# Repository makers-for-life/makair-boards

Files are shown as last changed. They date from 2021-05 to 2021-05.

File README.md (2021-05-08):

# MakAir Boards

## Components

| Part | Version | Last Changelog | Ready? | Schematics |
| ---- | ------- | -------------- | ------ | ---------- |
| [Pinch Valve Controller](./src/pinch-valve-controller) | V1 | Initial design | ✅ | [view schematic](./src/pinch-valve-controller/schematics/V1/1782SC001_01.pdf)
| [Raspberry Pi RTC](./src/raspberry-pi-rtc) | V1 | Initial design | ✅ | none
| [SFM 3300 Adapter](./src/sfm-3300-adapter) | V1 | Initial design | ✅ | none

## Renders

### The "Pinch Valve Controller"

<p align="center">
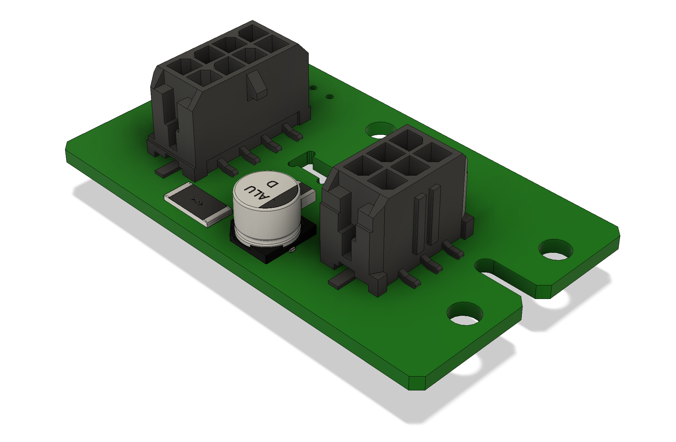
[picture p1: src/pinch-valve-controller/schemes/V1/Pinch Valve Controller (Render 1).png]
Pinch Valve Controller Render
  
</p>

### The "Raspberry Pi RTC"

<p align="center">
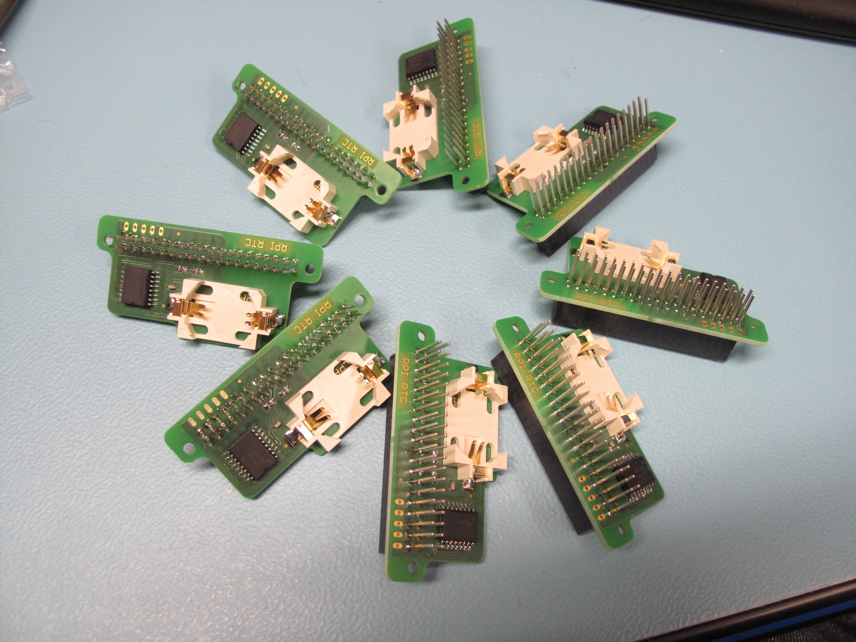
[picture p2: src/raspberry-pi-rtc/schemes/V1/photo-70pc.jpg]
Raspberry Pi RTC Photo
  
</p>

### The "SFM 3300 Adapter"

<p align="center">
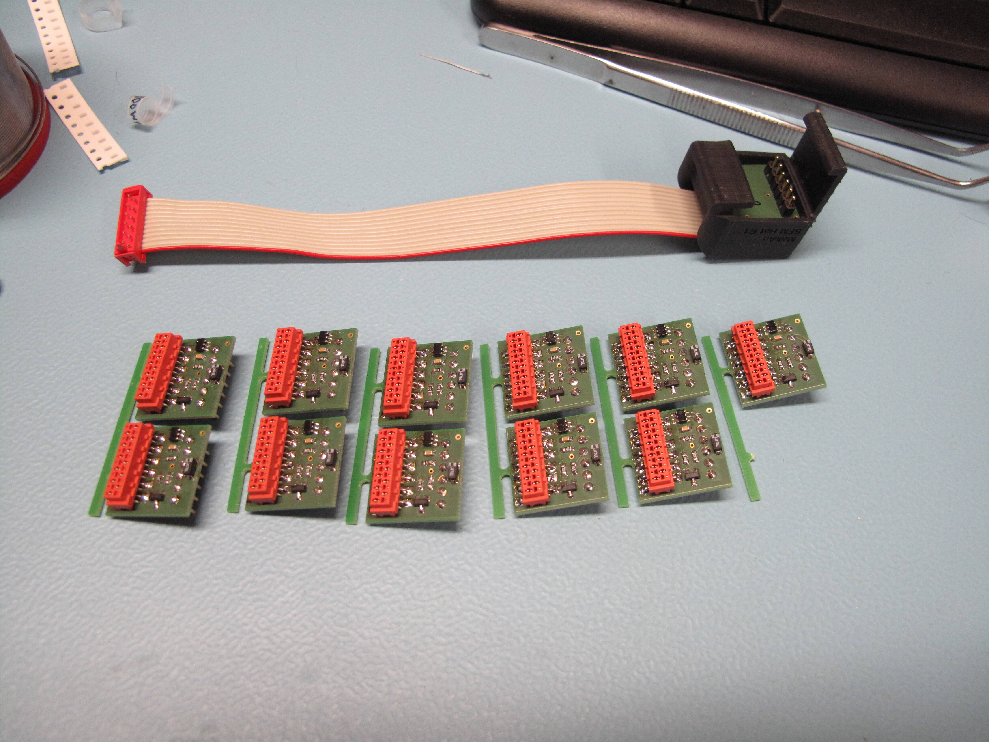
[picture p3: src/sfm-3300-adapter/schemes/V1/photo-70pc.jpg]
SFM 3300 Adapter Photo
  
</p>

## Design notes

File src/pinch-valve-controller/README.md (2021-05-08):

# Pinch Valve Controller

## Versions

| Version | Last Changelog | Ready? |
| ------- | -------------- | ------ |
| V1 | Initial design | ✅

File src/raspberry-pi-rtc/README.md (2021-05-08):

# Raspberry Pi RTC

## Versions

| Version | Last Changelog | Ready? |
| ------- | -------------- | ------ |
| V1 | Initial design | ✅

## Notes

This RTC HAT was designed to avoid any conflict between Raspberry Pi touchscreen and RTC. All the RTC you can find are connected on SDA3/SCL3 of the Raspberry 4. But the touchscreen is already connected to this port, and there is some random issues.

So, this small board is designed to connect a DS3231 on I2C6 of the Raspberry 4 (pin 15 and 16).

### How to setup RTC on I2C6 of Raspberry 4

Make sure that the Raspberry Pi is up to date:

```
sudo apt update
sudo apt upgrade
sudo reboot
sudo rpi-update
```

* Append to `/boot/config.txt`:

`dtoverlay=i2c6`

* Make a new DTC from the existing RTC one (named `i2c6-rtc`);

`sudo dtc -I dtb -O dts /boot/overlays/i2c-rtc.dtbo -o /boot/overlays/i2c6-rtc.dts`

* Edit it to change `i2c_arm` to `i2c6`:

`sudo sed -i "s/i2c_arm/i2c6/g" /boot/overlays/i2c6-rtc.dts`

* Recompile it:

`sudo dtc -I dts -O dtb /boot/overlays/i2c6-rtc.dts -o /boot/overlays/i2c6-rtc.dtbo`

* Append to `/boot/config.txt`:

`dtoverlay=i2c6-rtc,ds3231`

After reboot, check `dmesg`:

```
dmesg | grep rtc
[    5.883603] rtc : registered as rtc0
```

If battery is low:

```
[  42.117539] rtc: low voltage detected, time is unreliable
```

Now write current time into the RTC, make sure your Raspberry Pi clock is synchronized, using `date`, then `sudo hwclock -w` to write current date into the RTC.

On Arch Linux, you have to create a script on startup to read RTC time during the boot:

```
cat > /etc/systemd/system/rtc.service << ENDRTCSERVICE
[Unit]
Description=RTClock
Before=network.target

[Service]
ExecStart=/usr/bin/hwclock -s
Type=oneshot
[Install]
WantedBy=multi-user.target
ENDRTCSERVICE
```

Then enable this service:

```
systemctl enable rtc
systemctl start rtc
```

Reboot, then check everything is OK:

```
journalctl -u rtc
```

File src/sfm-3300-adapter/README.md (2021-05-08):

# SFM 3300 Adapter

## Versions

| Version | Last Changelog | Ready? |
| ------- | -------------- | ------ |
| V1 | Initial design | ✅

## Notes

This little board provides a convenient way to interface a Sensirion SFM3300 to the red micromatch connector of the Motherboard.

As soon I2C clock remains low, the sensor is shutdown. This allows easy hard reset.

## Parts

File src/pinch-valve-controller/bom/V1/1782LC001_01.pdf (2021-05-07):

Designation : INTERFACE MOTEUR | | Author by : olbonneau
Customer : TRONICO | Date : 23/04/2020 | Signature :
Reference : 1782LC001 | Revision : 01A | Verified by : P. Boiziau
Customer Reference : 099 | | Signature :
Designator | ID_RnD | CODE_PC | Quantity | Done
* | | C1 | 21U00041 | 002504131A | COND_ALUM CMS D:6.3mm | 47uF 50V 20% 680mR -55°C/+105°C | PANASONIC EEEFT1H470AP | 1
* | | C2,C3 | 23U00347 | 00280K614A | COND_CERAM CMS 0603 X5R | 1uF 50V 10% -55°C/+85°C | TAIYO YUDEN UMK107BJ105KA-T TDK CGA3E3X5R1H105K080AB | 2
* | | C4 | 23U00036 | 002806597A | COND_CERAM CMS 0603 X7R | 100nF 50V 10% -55°C/+125°C | KEMET C0603C104K5RAC VISHAY VJ0603Y104KXAAT AVX 06035C104KAT2A | 1
* | | C6 | 23U00488 | 00280K521A | COND_CERAM CMS 1206 X5R | 10uF 50V 10% -55°C/+85°C | MURATA GRM31CR61H106KA12L | 1
* | | ET1 | G1U00004 | - | ETIQUETTE IDENTIFICATION | 1782ET001 | PLAN 1782ET001 IND01 | 1
| * | - | - | CONSOM1071 | ETIQU ETIQU POLYIMIDE AMBRE MAT | | BRADY THT-46-724-10 | 1
* | | J1 | A7U00233 | 005168584A-RD | CONNECT MICRO-FIT CMS 2x4PTS | EMBASE RECT MALE DROIT -40°C/+105°C | MOLEX 43045-0818 | 1
* | | J2 | A7U00234 | 005168586A-RD | CONNECT MICRO-FIT CMS 2x3PTS | EMBASE RECT MALE DROIT -40°C/+105°C | MOLEX 43045-0618 | 1
* | | L1 | 42U00104 | 003114209A-RD | SELF CMS 2.5x2mm | 1.5uH 20% 3.1A -55°C/+125°C | VISHAY IHHP1008ABER1R5M01 | 1
* | | PCB1 | I1U00004 | 00590G849A | CIRCUIT IMPRIME INTERFACE MOTEUR | 1782CI001 | SPECIF 1782PCB001 IND01 PLANS 1782CI001 IND01 GERBERS 1782GER001 IND01 | 1 | Mise en panneau faite par le fournisseur
* | | R1 | 11U00106 | 00140AA309A-RD | REST CMS 0603 100PPM | 220R 1/10W 1% -55°C/+155°C | YAGEO RC0603FR-07220RL | 1
* | | R2,R7 | 11U00108 | 00140D722A | REST CMS 0603 100PPM | 10kR 1/10W 1% -55°C/+155°C | NEOHM CRG0603F10K YAGEO RC0603FR-0710KL VISHAY CRCW060310K0FKEA VISHAY CRCW060310K0FK@e3 | 2
* | | R3 | 11U00053 | 00140AA3641A | REST CMS 0603 100PPM | 330kR 1/10W 1% -55°C/+155°C | VISHAY CRCW0603330KFKEA | 1
* | | R4 | 11U00279 | 00140Q148A-RD | REST CMS 0805 100PPM | 270R 1/8W 1% -55°C/+155°C | YAGEO RC0805FR-07270RL | 1
* | | R5 | | | | | | NC
* | | R6 | 11U00688 | 00140AA3979A | REST CMS 0603 100PPM | 5.49kR 1/10W 1% -55°C/+155°C | YAGEO RC0603FR-075K49L | 1
* | | R8 | 11U01009 | 00140B064A | REST CMS 2512 100PPM | 1R 1.5W 1% 500V -55°C/+155°C | VISHAY CRCW25121R00FKEGHP | 1
* | | U1 | 61U00045 | 00480K448A-RD | CI_AOP_COMPAR CMS SOT23-5 | SINGLE COMP +2.7V/+5V R TO R -40°C/+85°C -65°C/+150°C | TEXAS INSTRUMENTS LMC7215IM5/NOPB | 1
* | | U2 | ECU00004 | 00480P154A | CAPTEUR_OPTO CMS 5.5x4x4 PHOTOTRANSISTOR | +1.0V/+1.4V NPN -40°C/+125°C -40°C/+125°C | VISHAY TCPT1350X01 | 1
Level | Reference designator | ID_RnD | Item Code | Description | Quantity | Commentary
1 | 2 | 3 | 4 | | | | Short Description | Long Description | Manufacturer & Part Number
Soudure : | SAC

26 RUE DU BOCAGE CS 20660
ST PHILBERT DE BOUAINE
85607 MONTAIGU CEDEX
Tél : +33 (0)2 51 41 91 35 Fax : +33 (0)2 51 41 94 27
ET68/D | STRICTEMENT CONFIDENTIEL TRONICO | 1/1

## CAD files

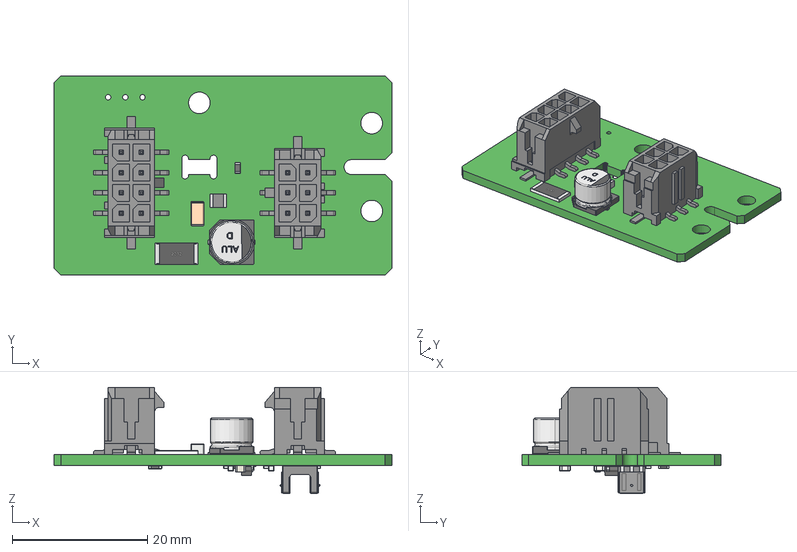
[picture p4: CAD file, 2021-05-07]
src/pinch-valve-controller/step/V1/1782CI001_01.step
50.0 x 29.5 x 15.7 mm
User_Library-SMD_RESISTOR-1
Extruded x 8
1206x160
0603x080 x 2
Corps x 7
Terminal x 14
Vishay_logo_-_1
Vishay_logo
SOT23-5-2
Fuss_1
Pins_1
K_X_F6rper_1
Beschriftung_1

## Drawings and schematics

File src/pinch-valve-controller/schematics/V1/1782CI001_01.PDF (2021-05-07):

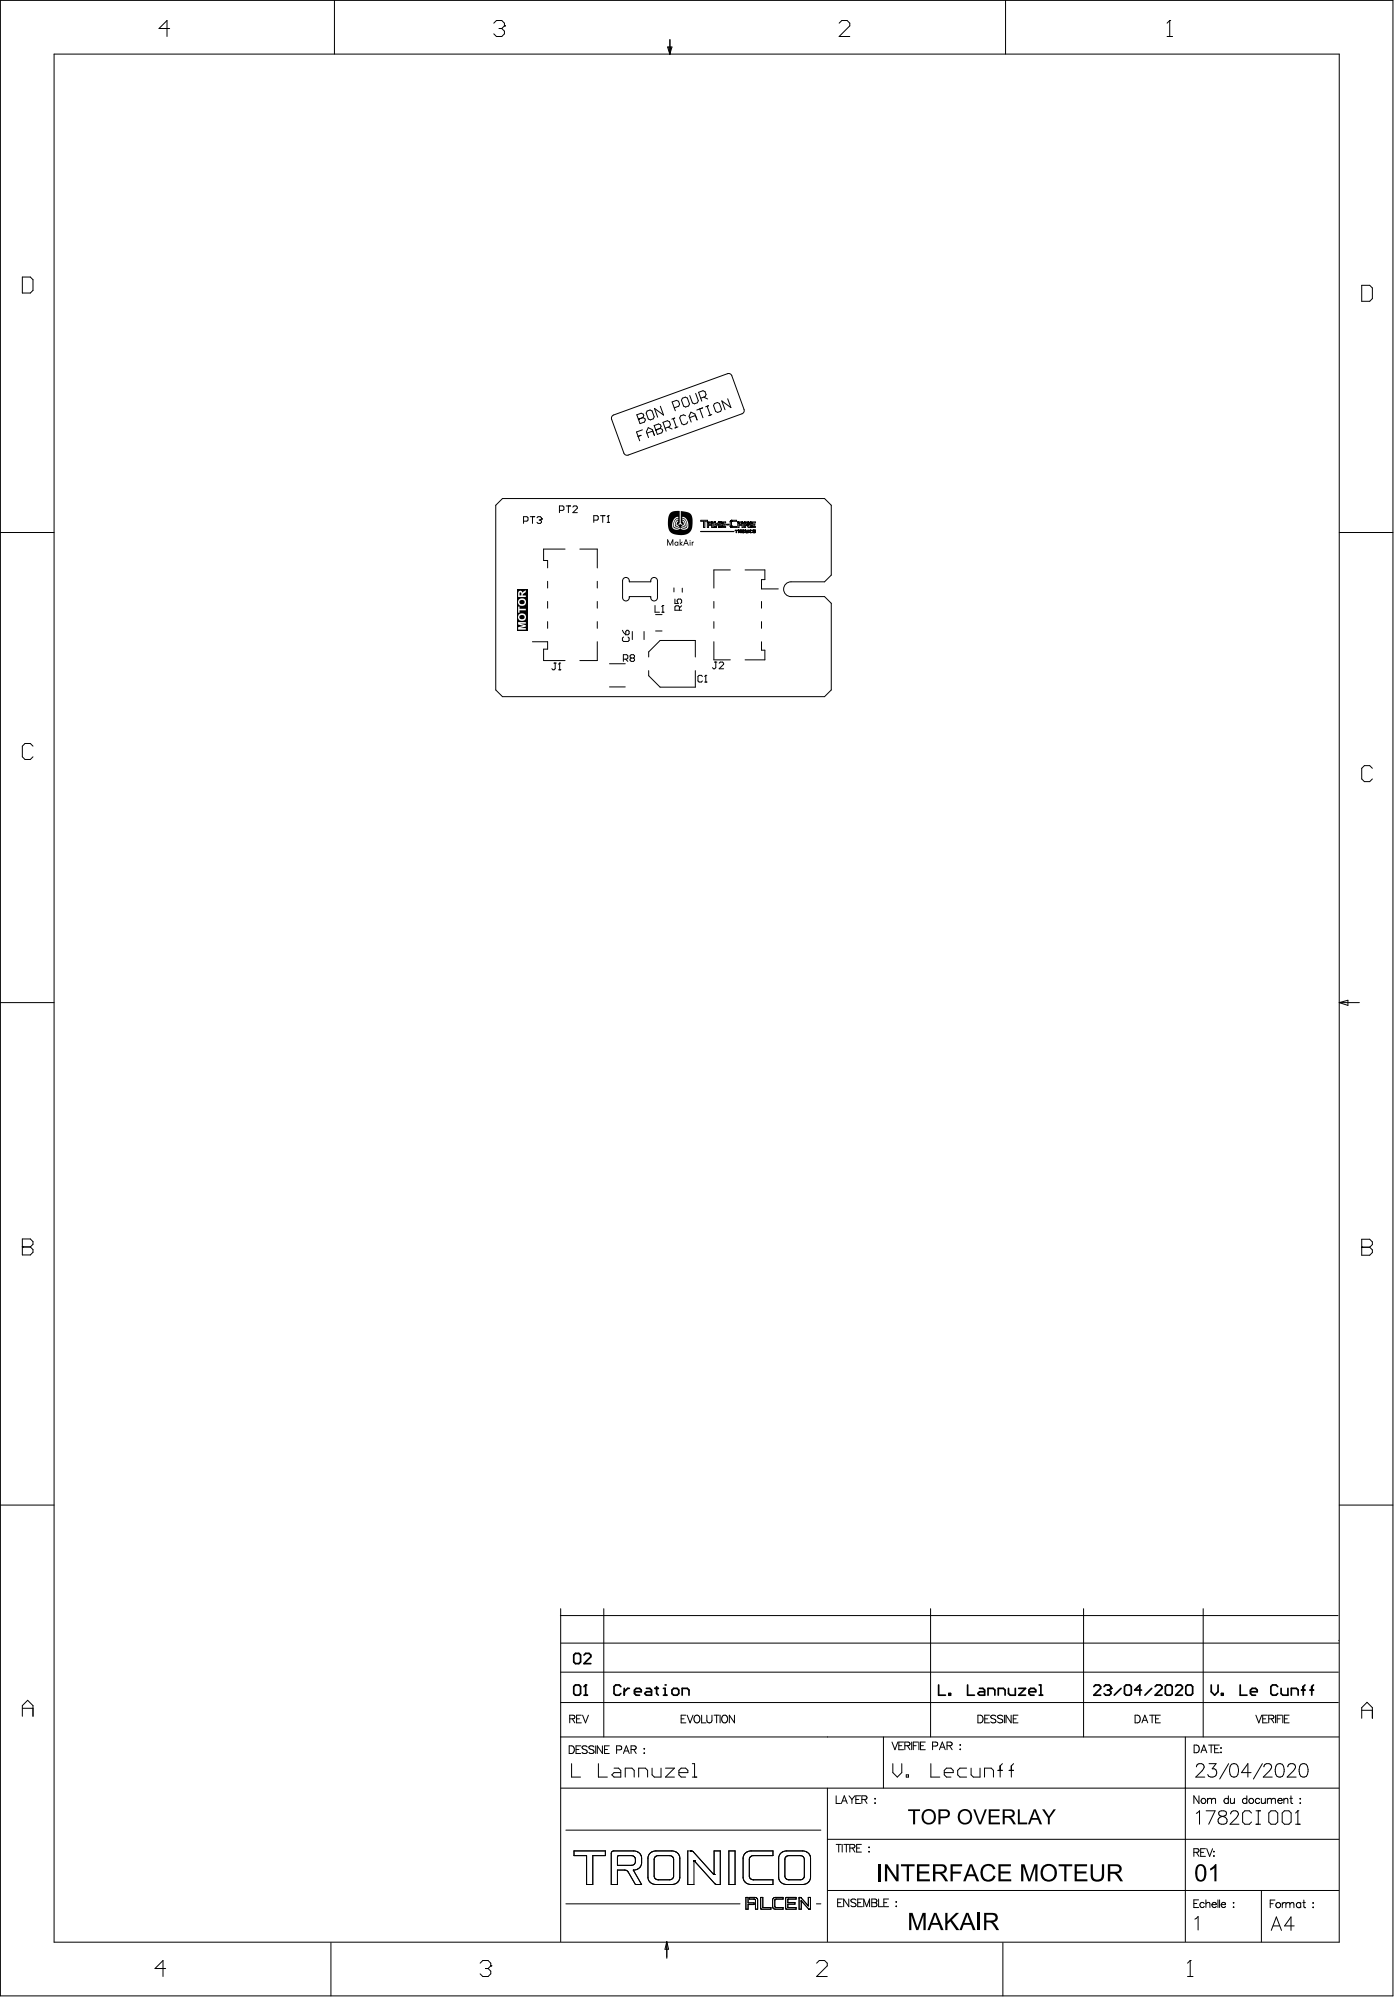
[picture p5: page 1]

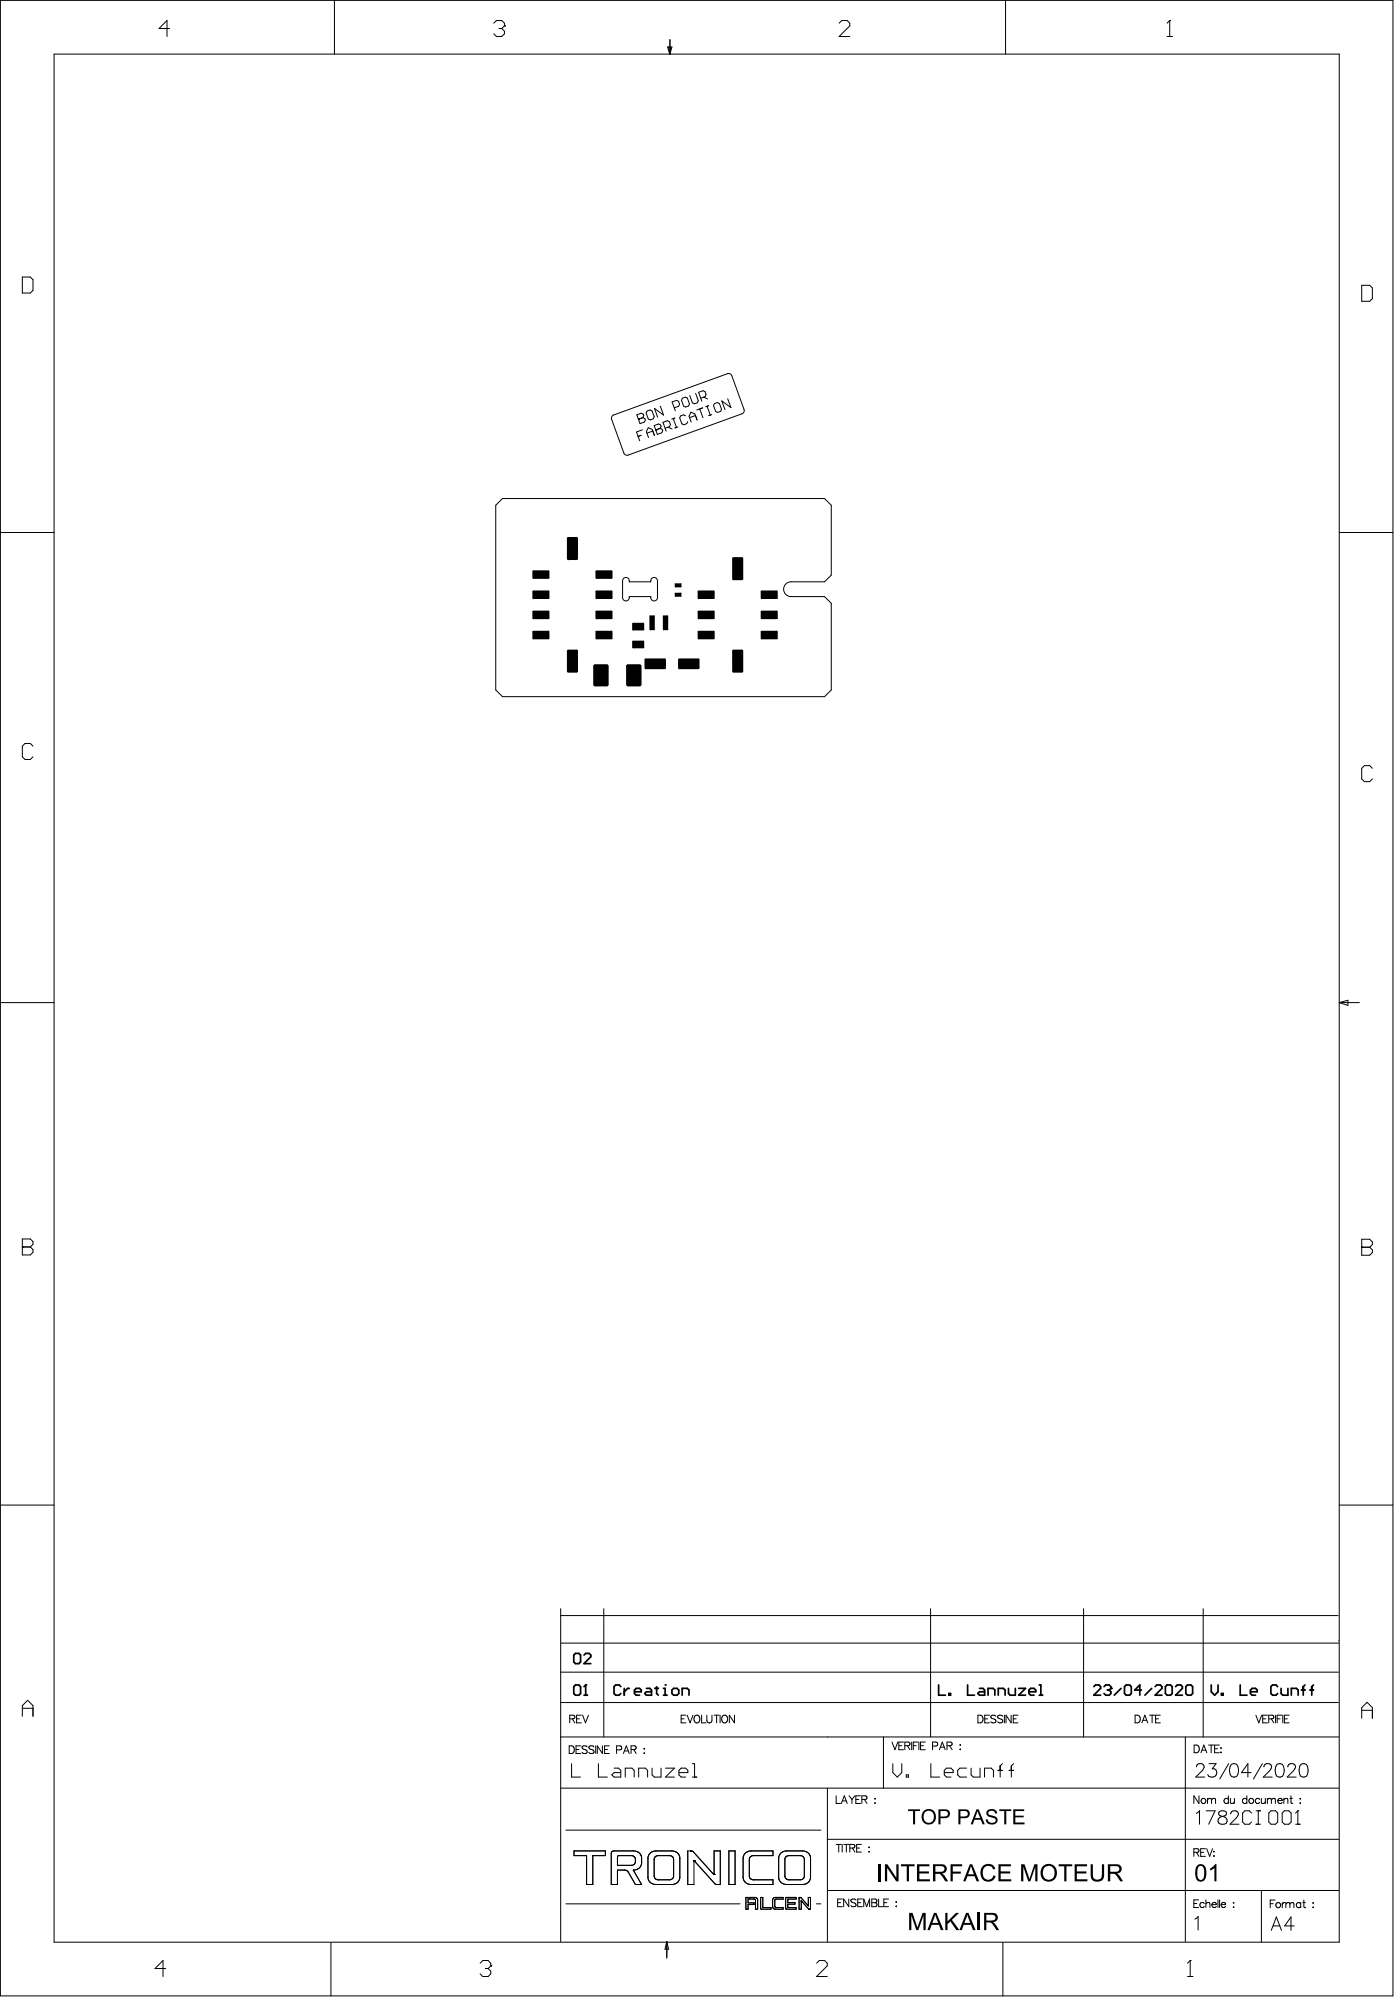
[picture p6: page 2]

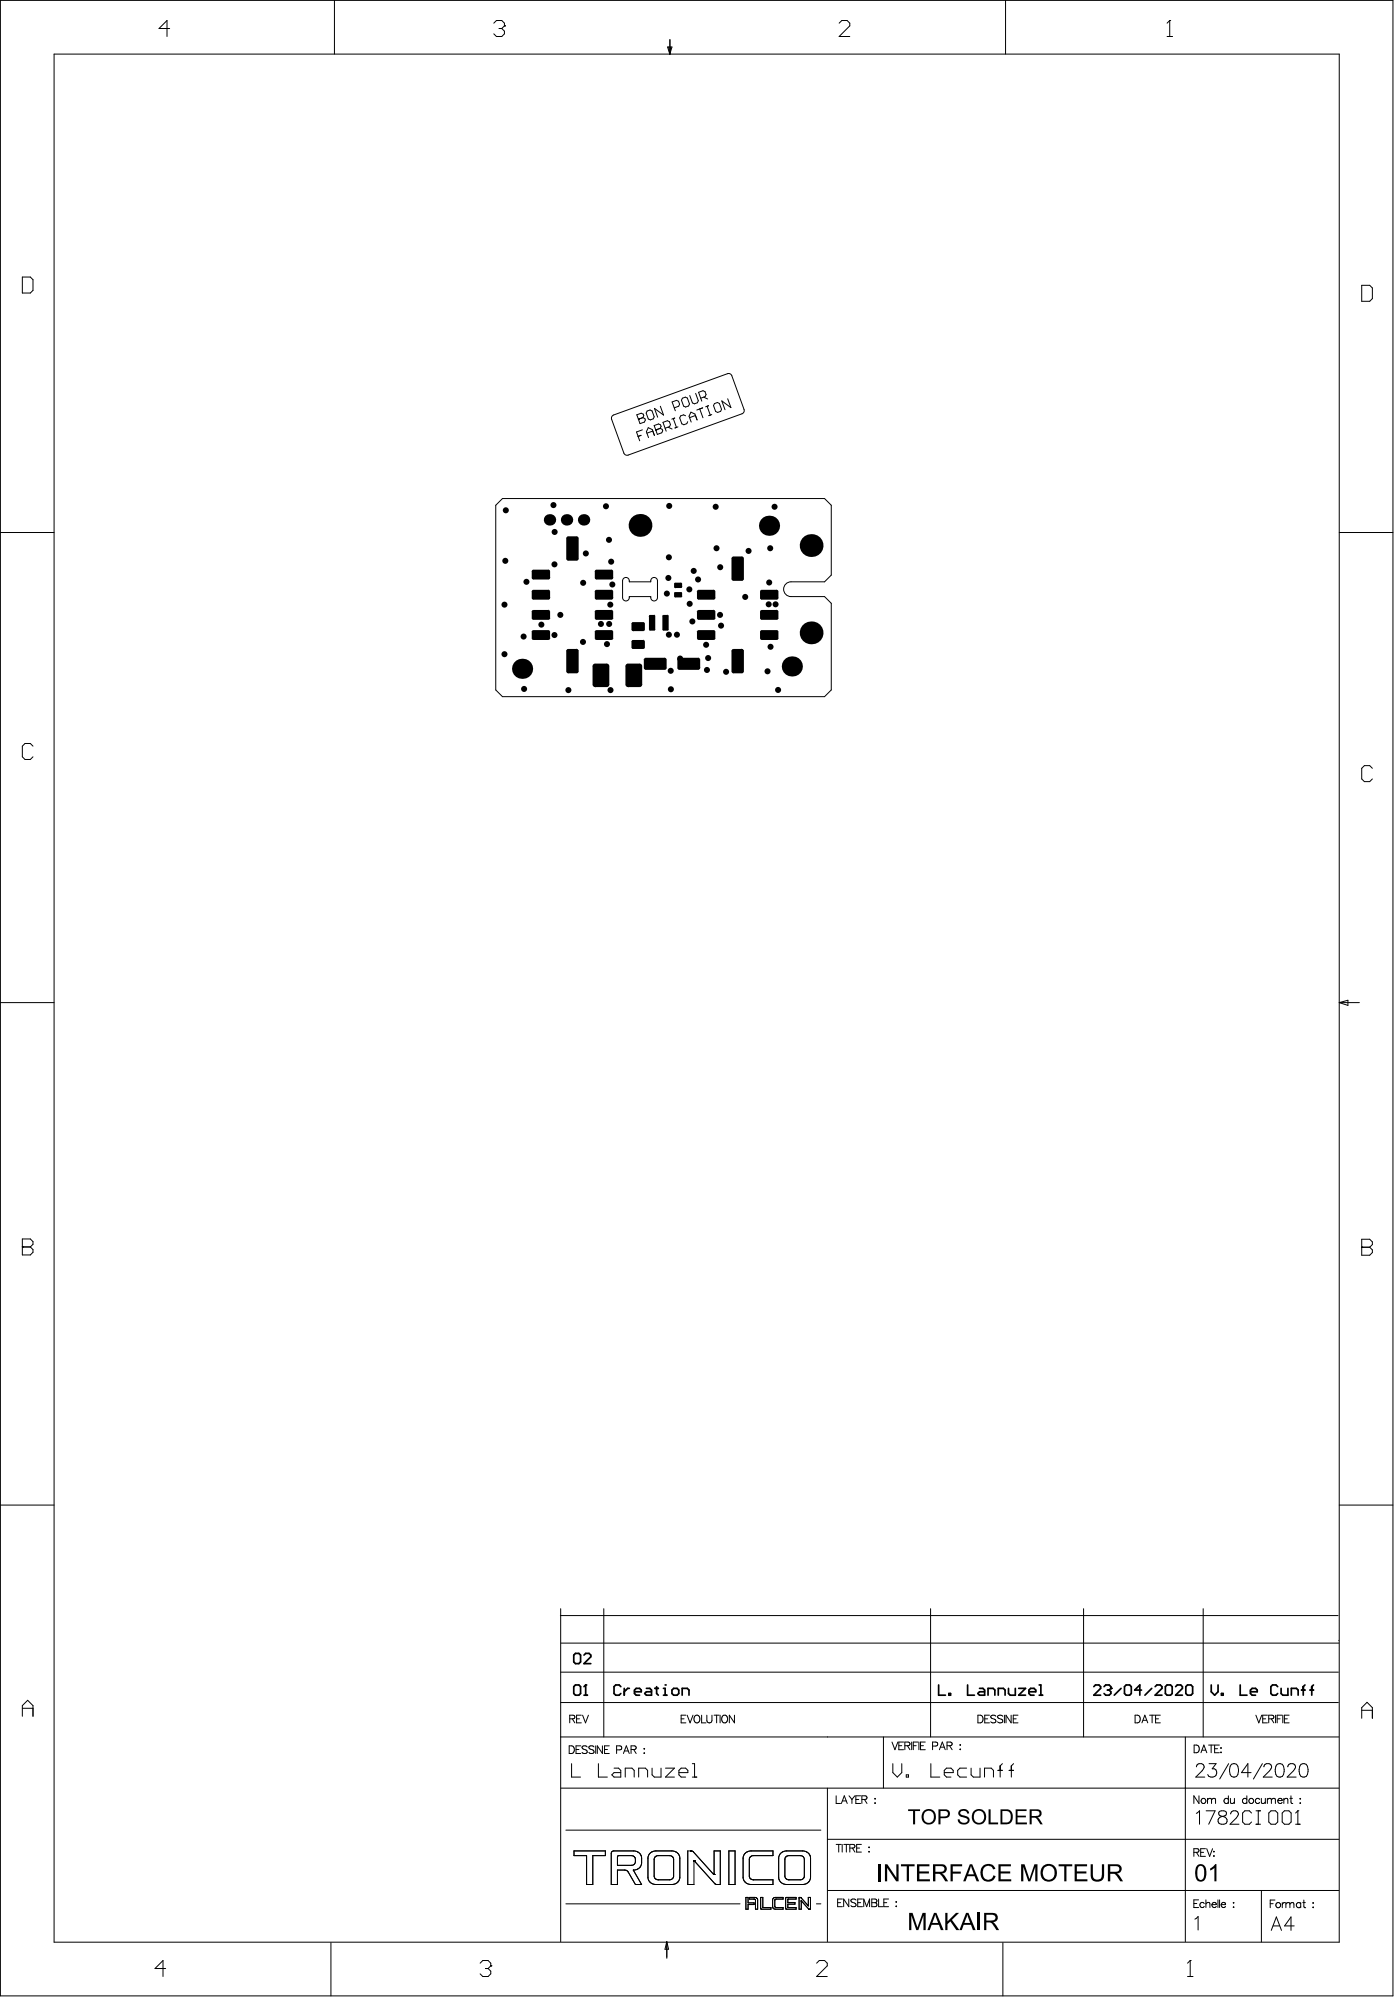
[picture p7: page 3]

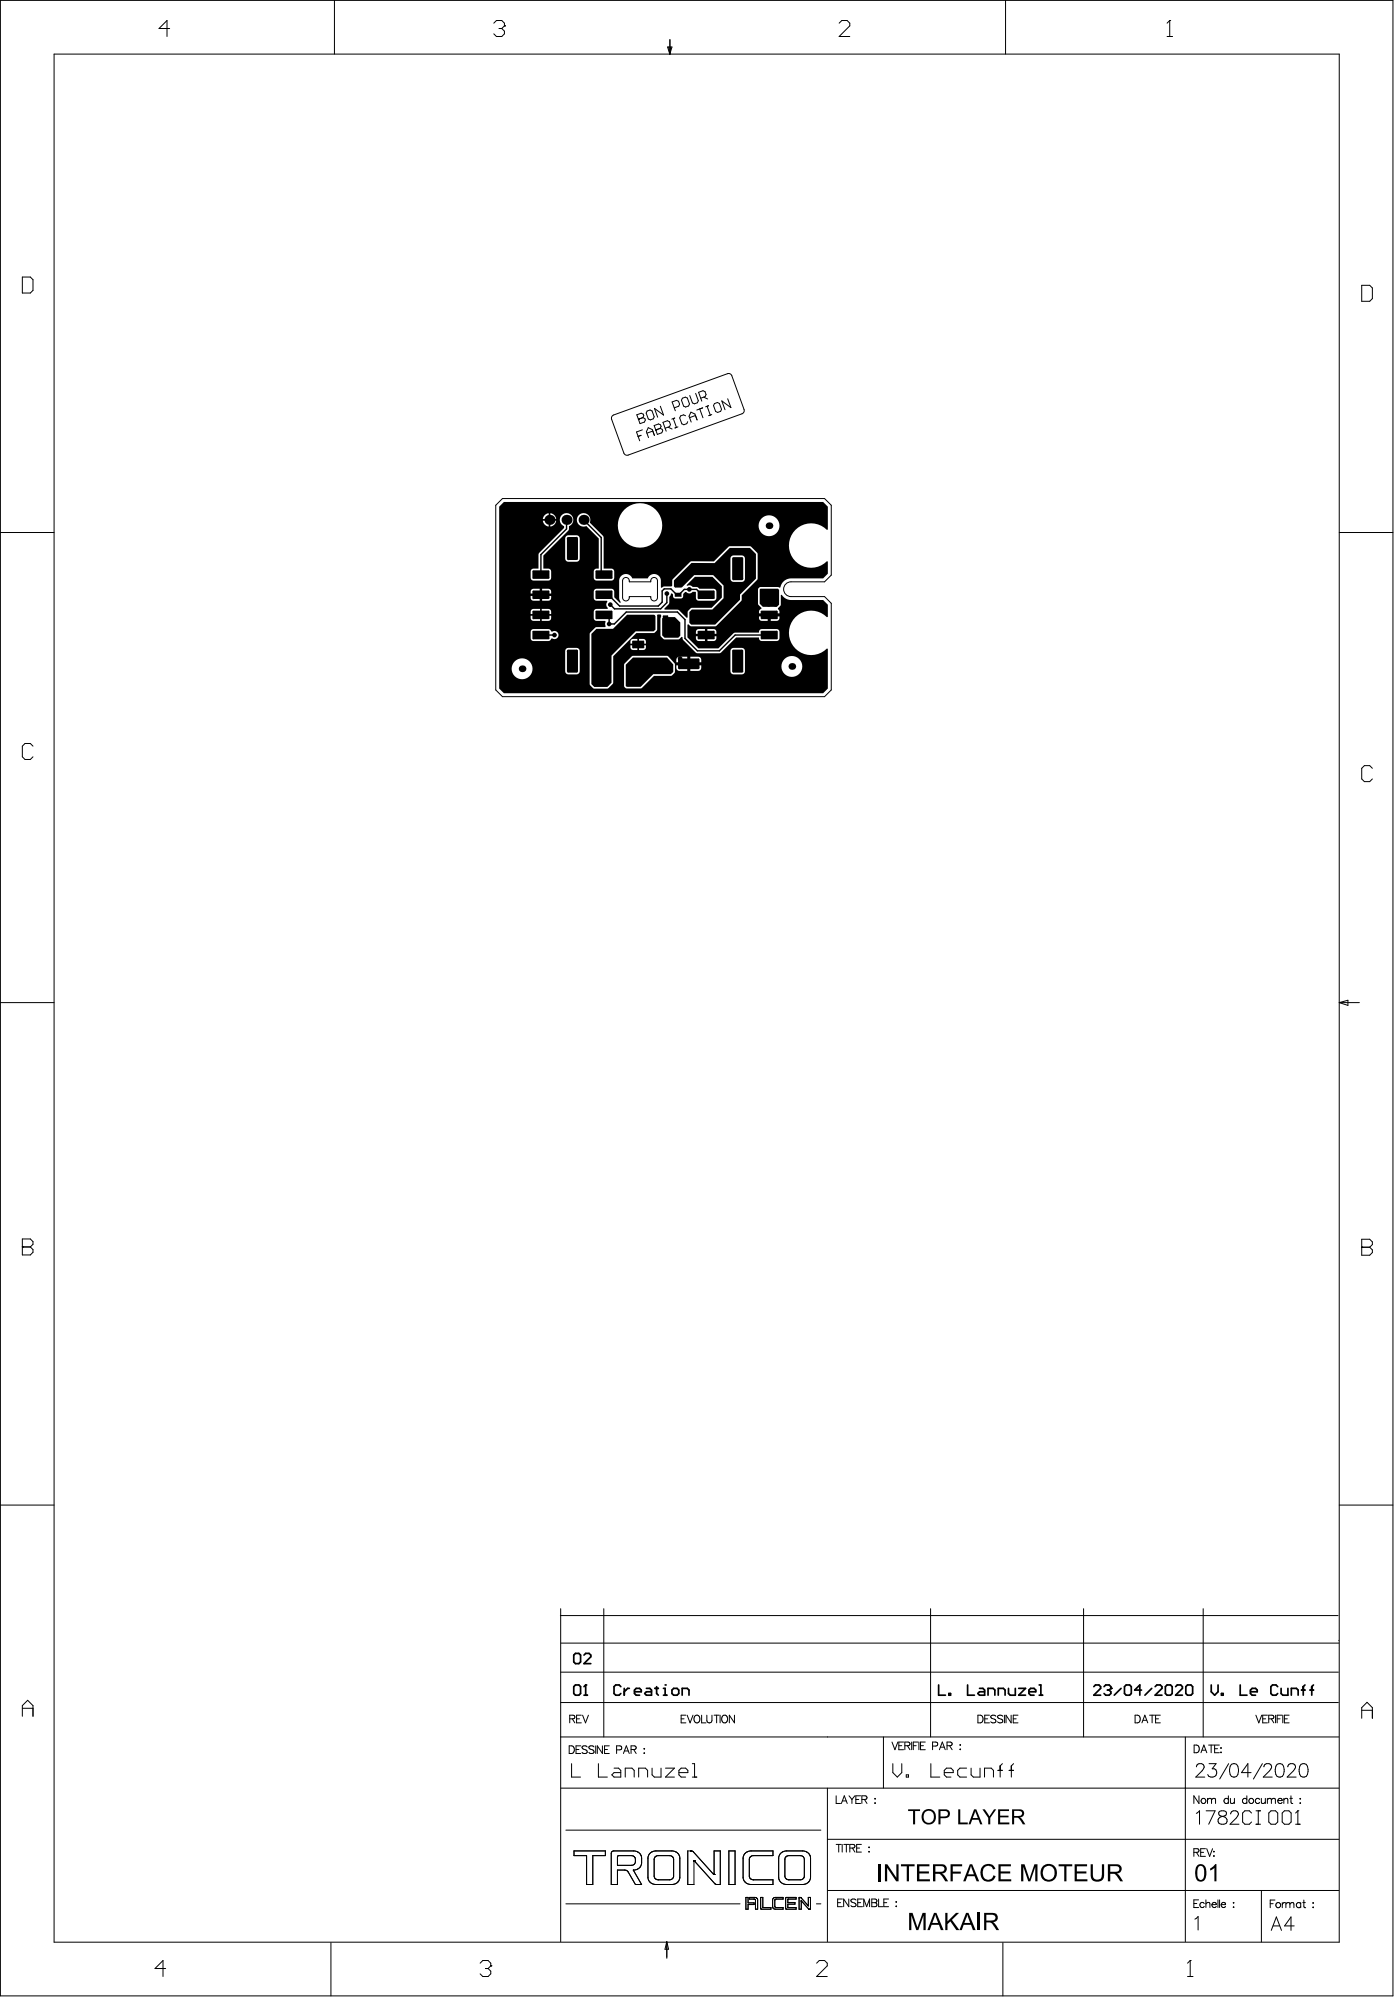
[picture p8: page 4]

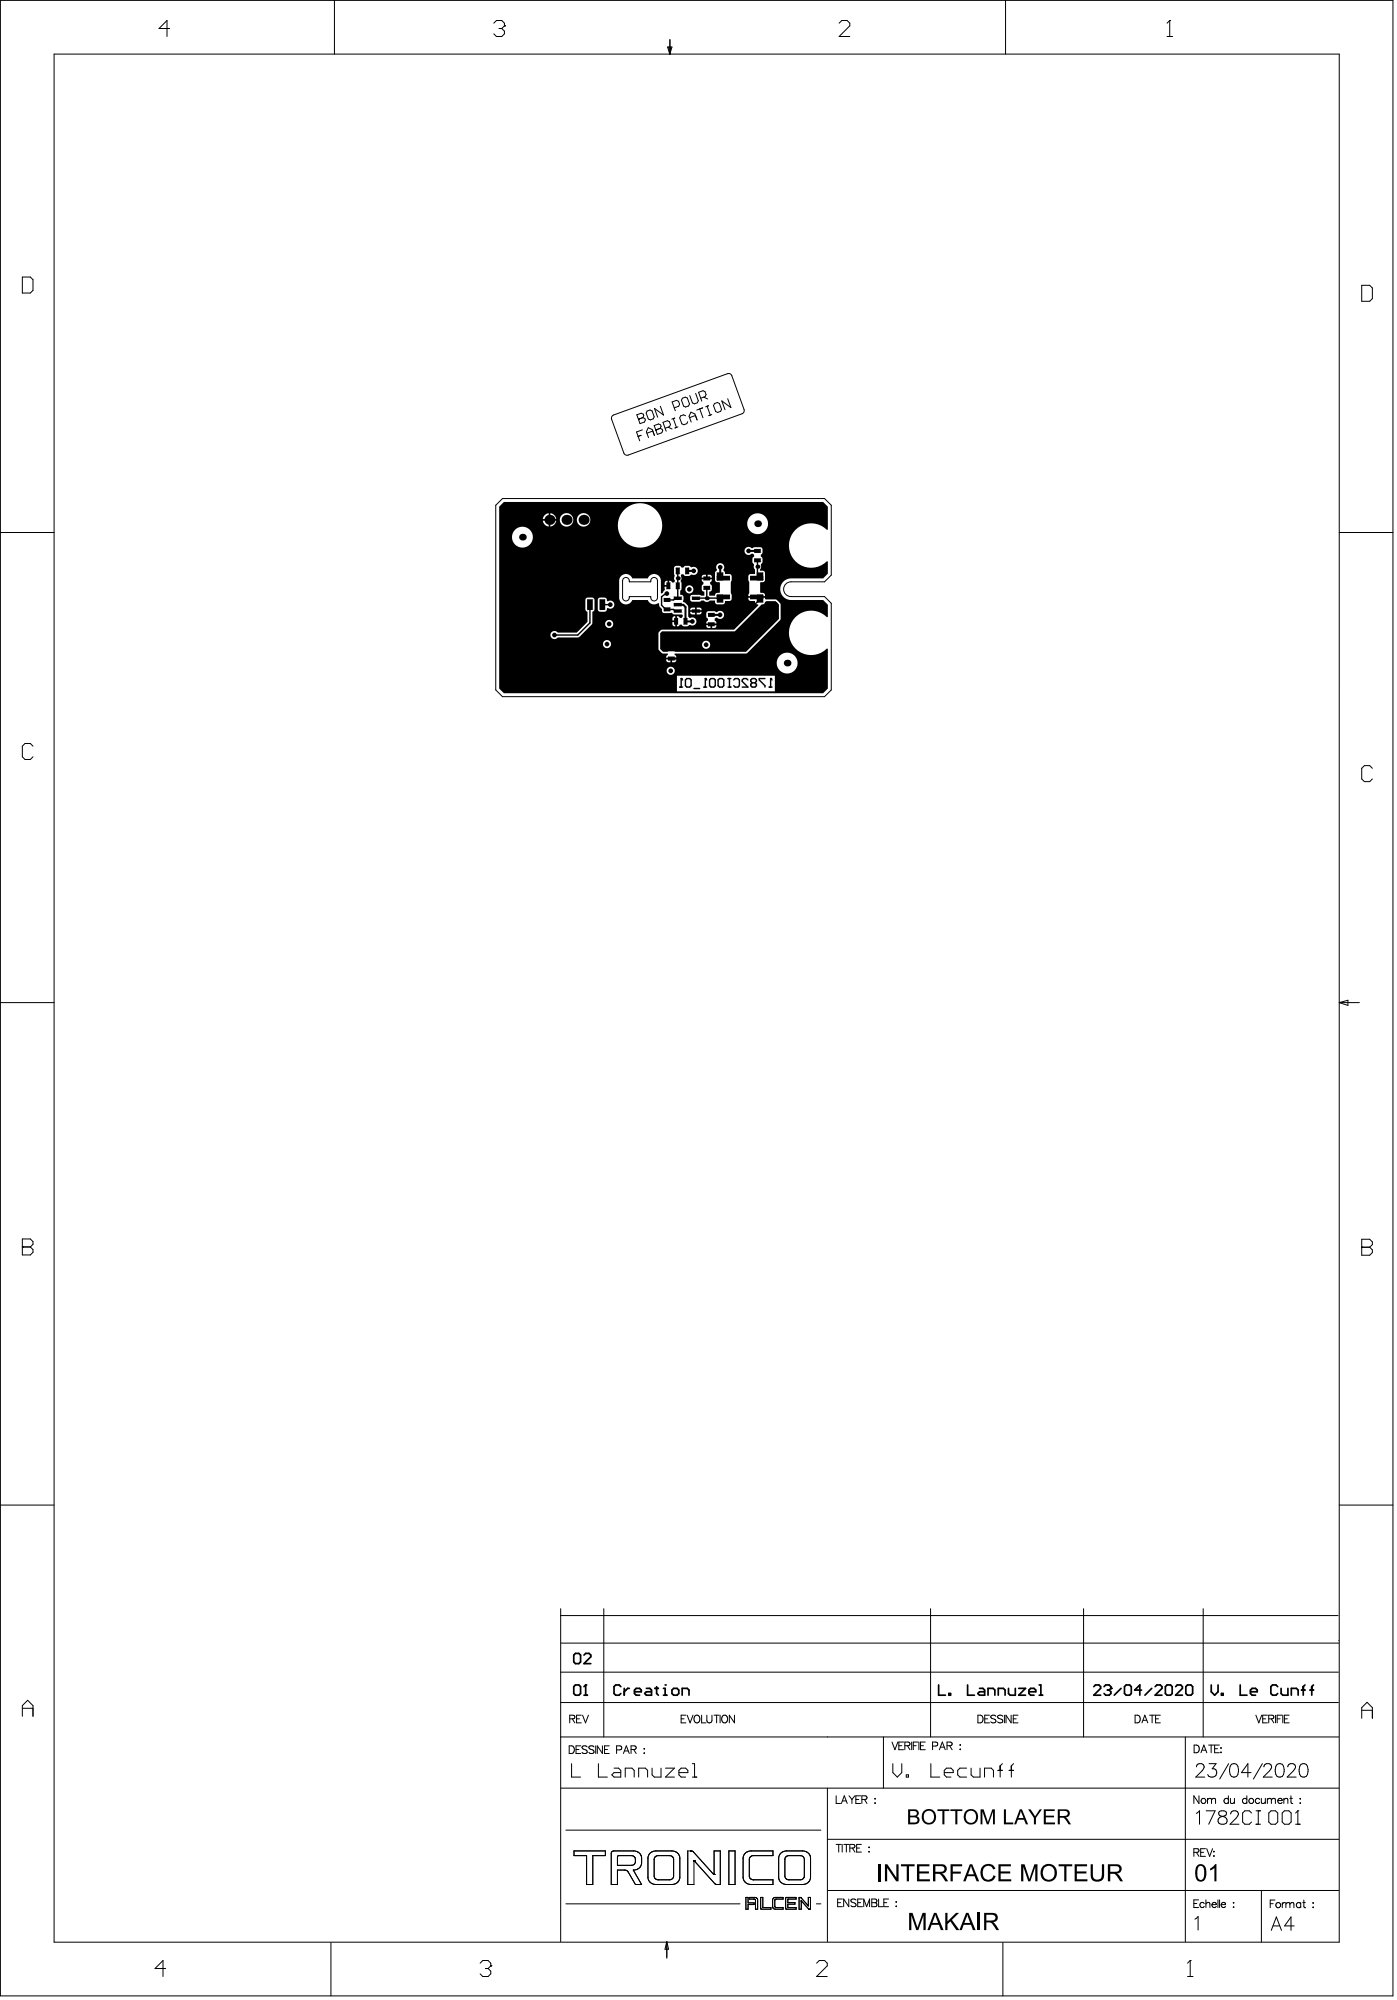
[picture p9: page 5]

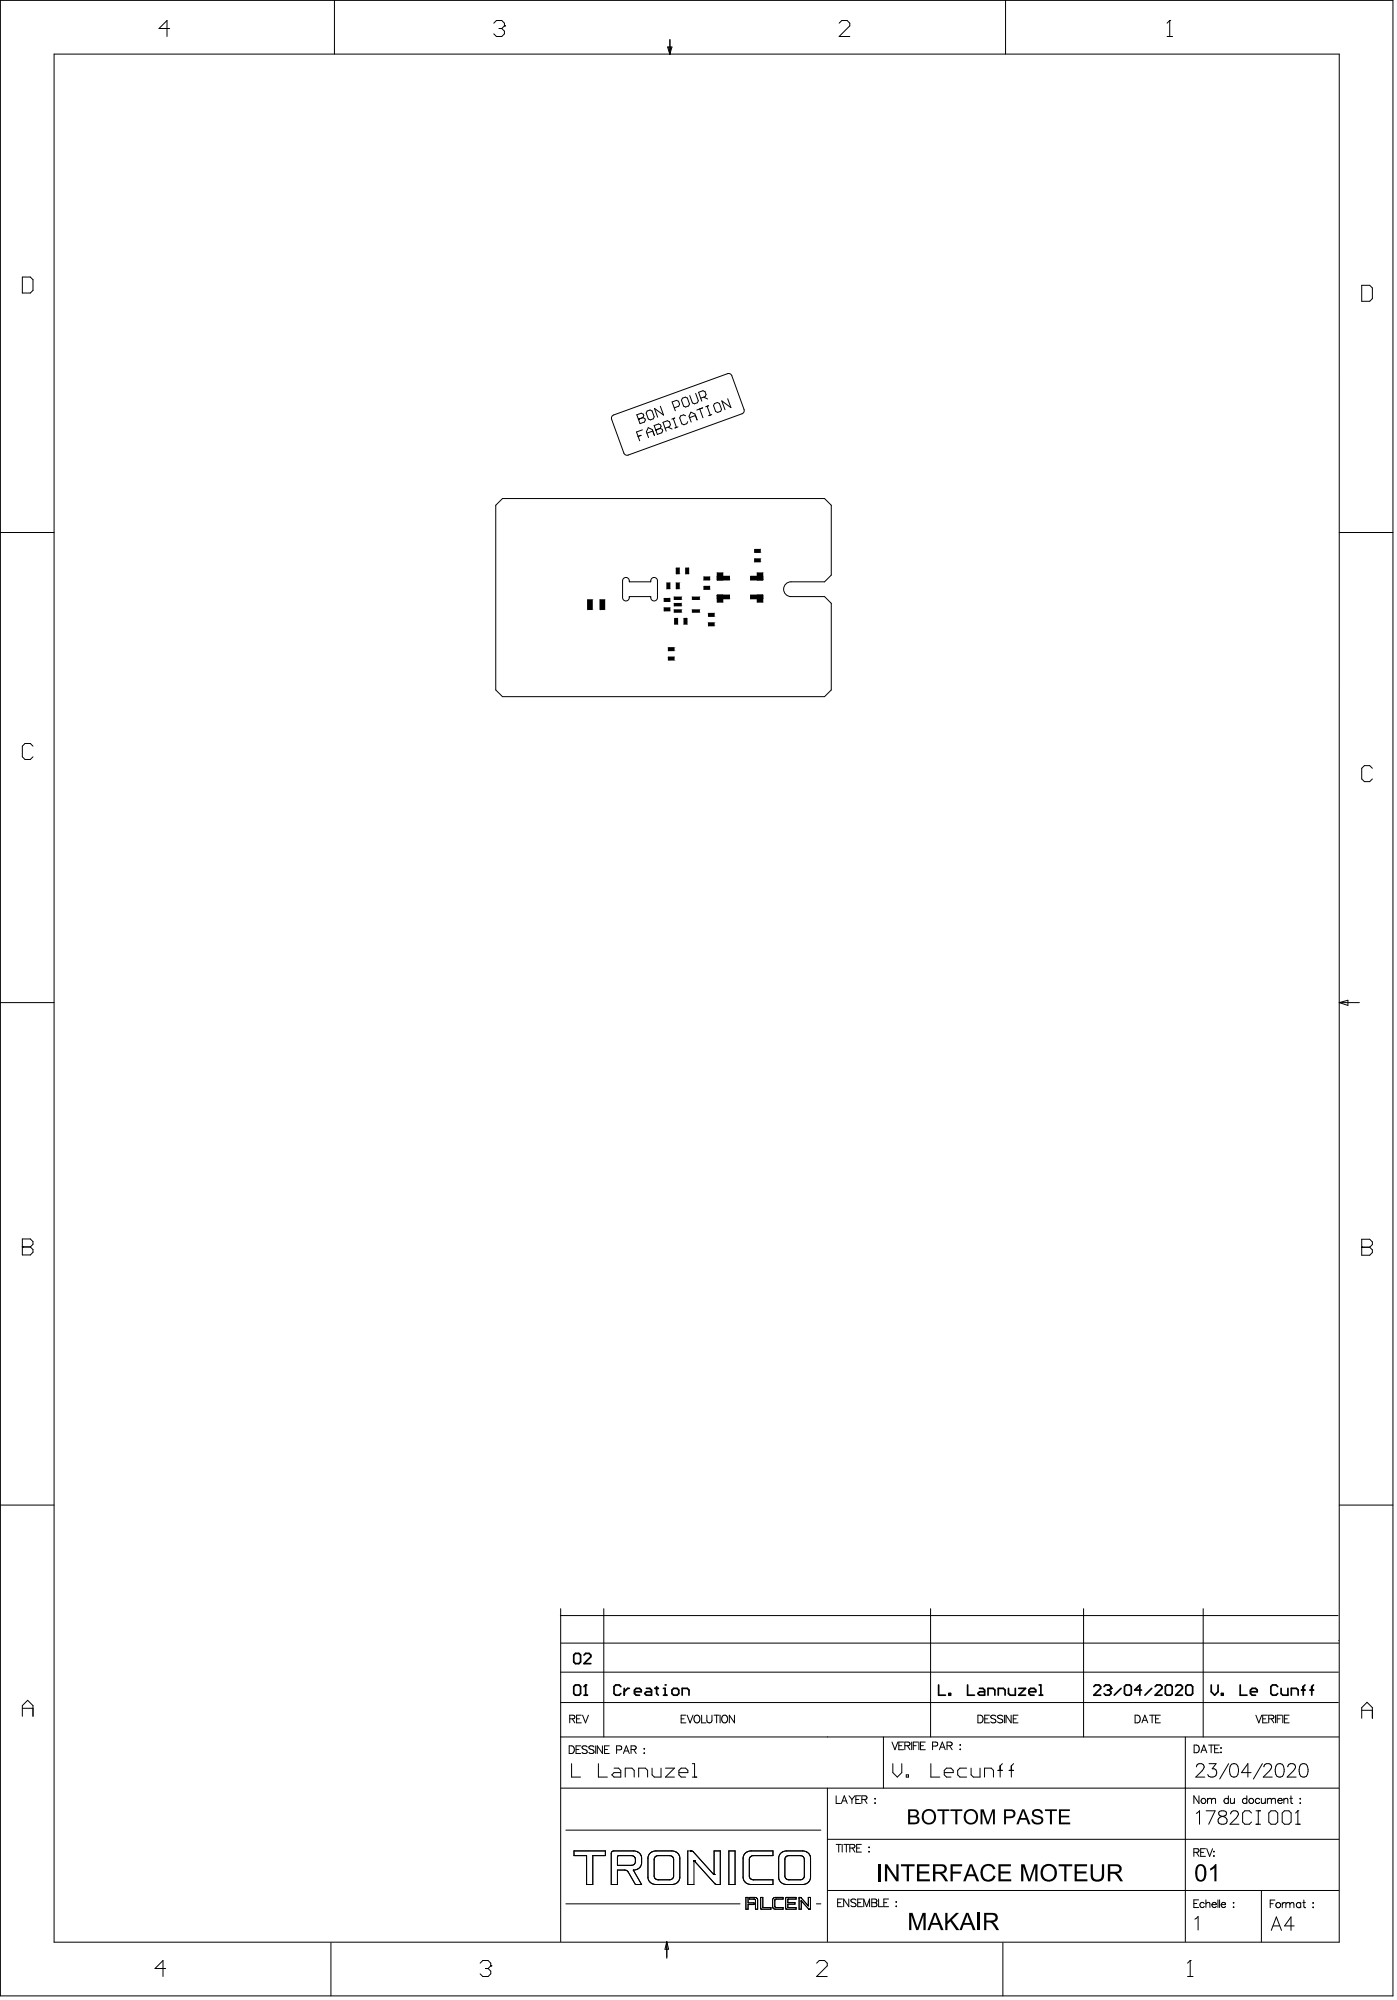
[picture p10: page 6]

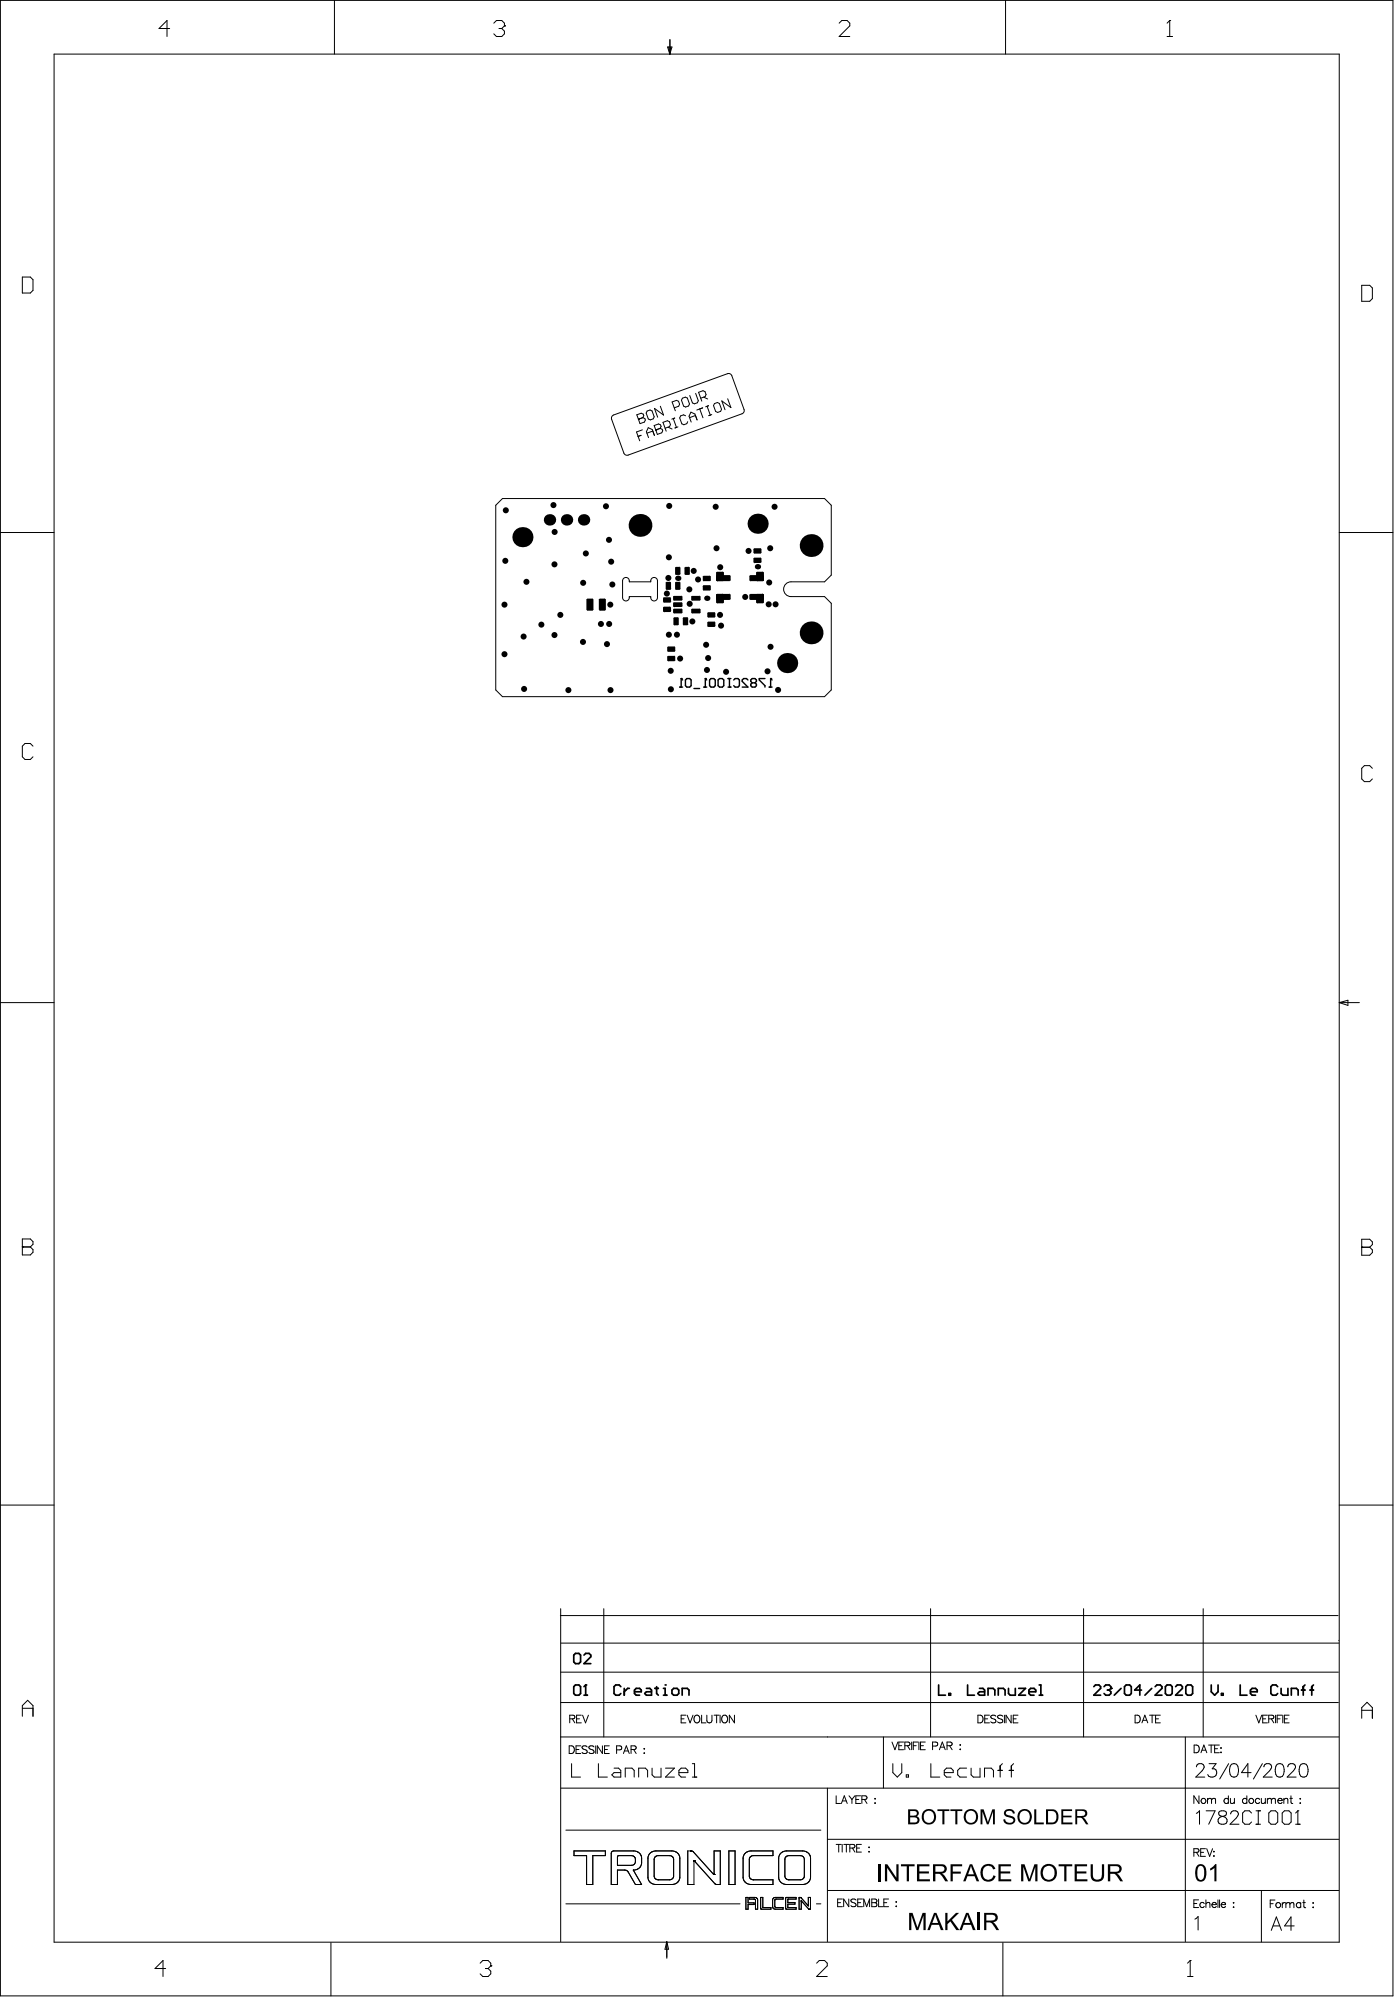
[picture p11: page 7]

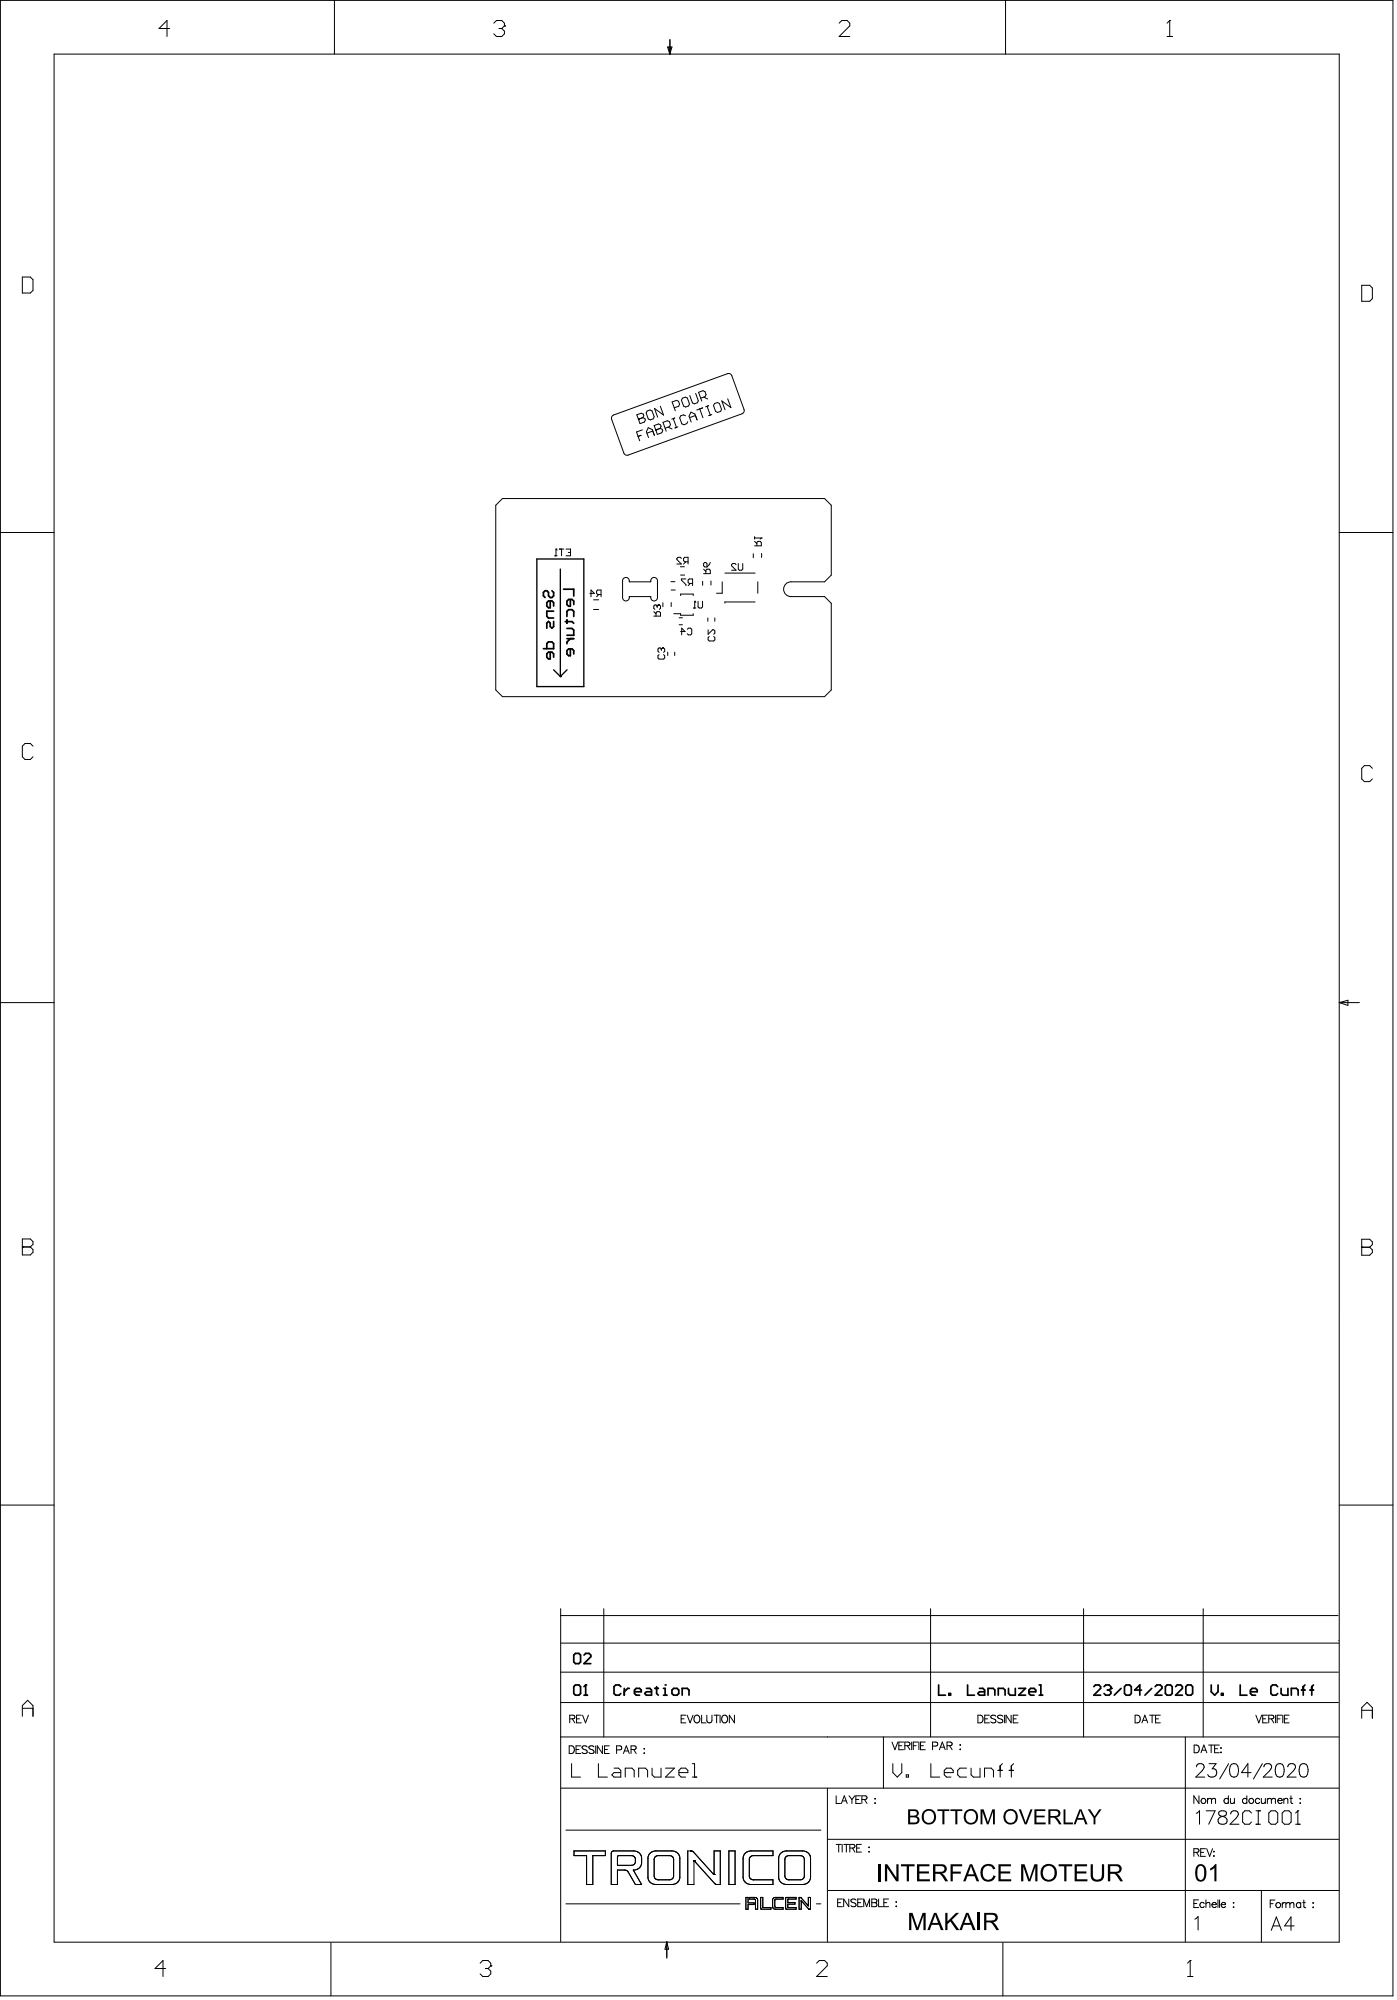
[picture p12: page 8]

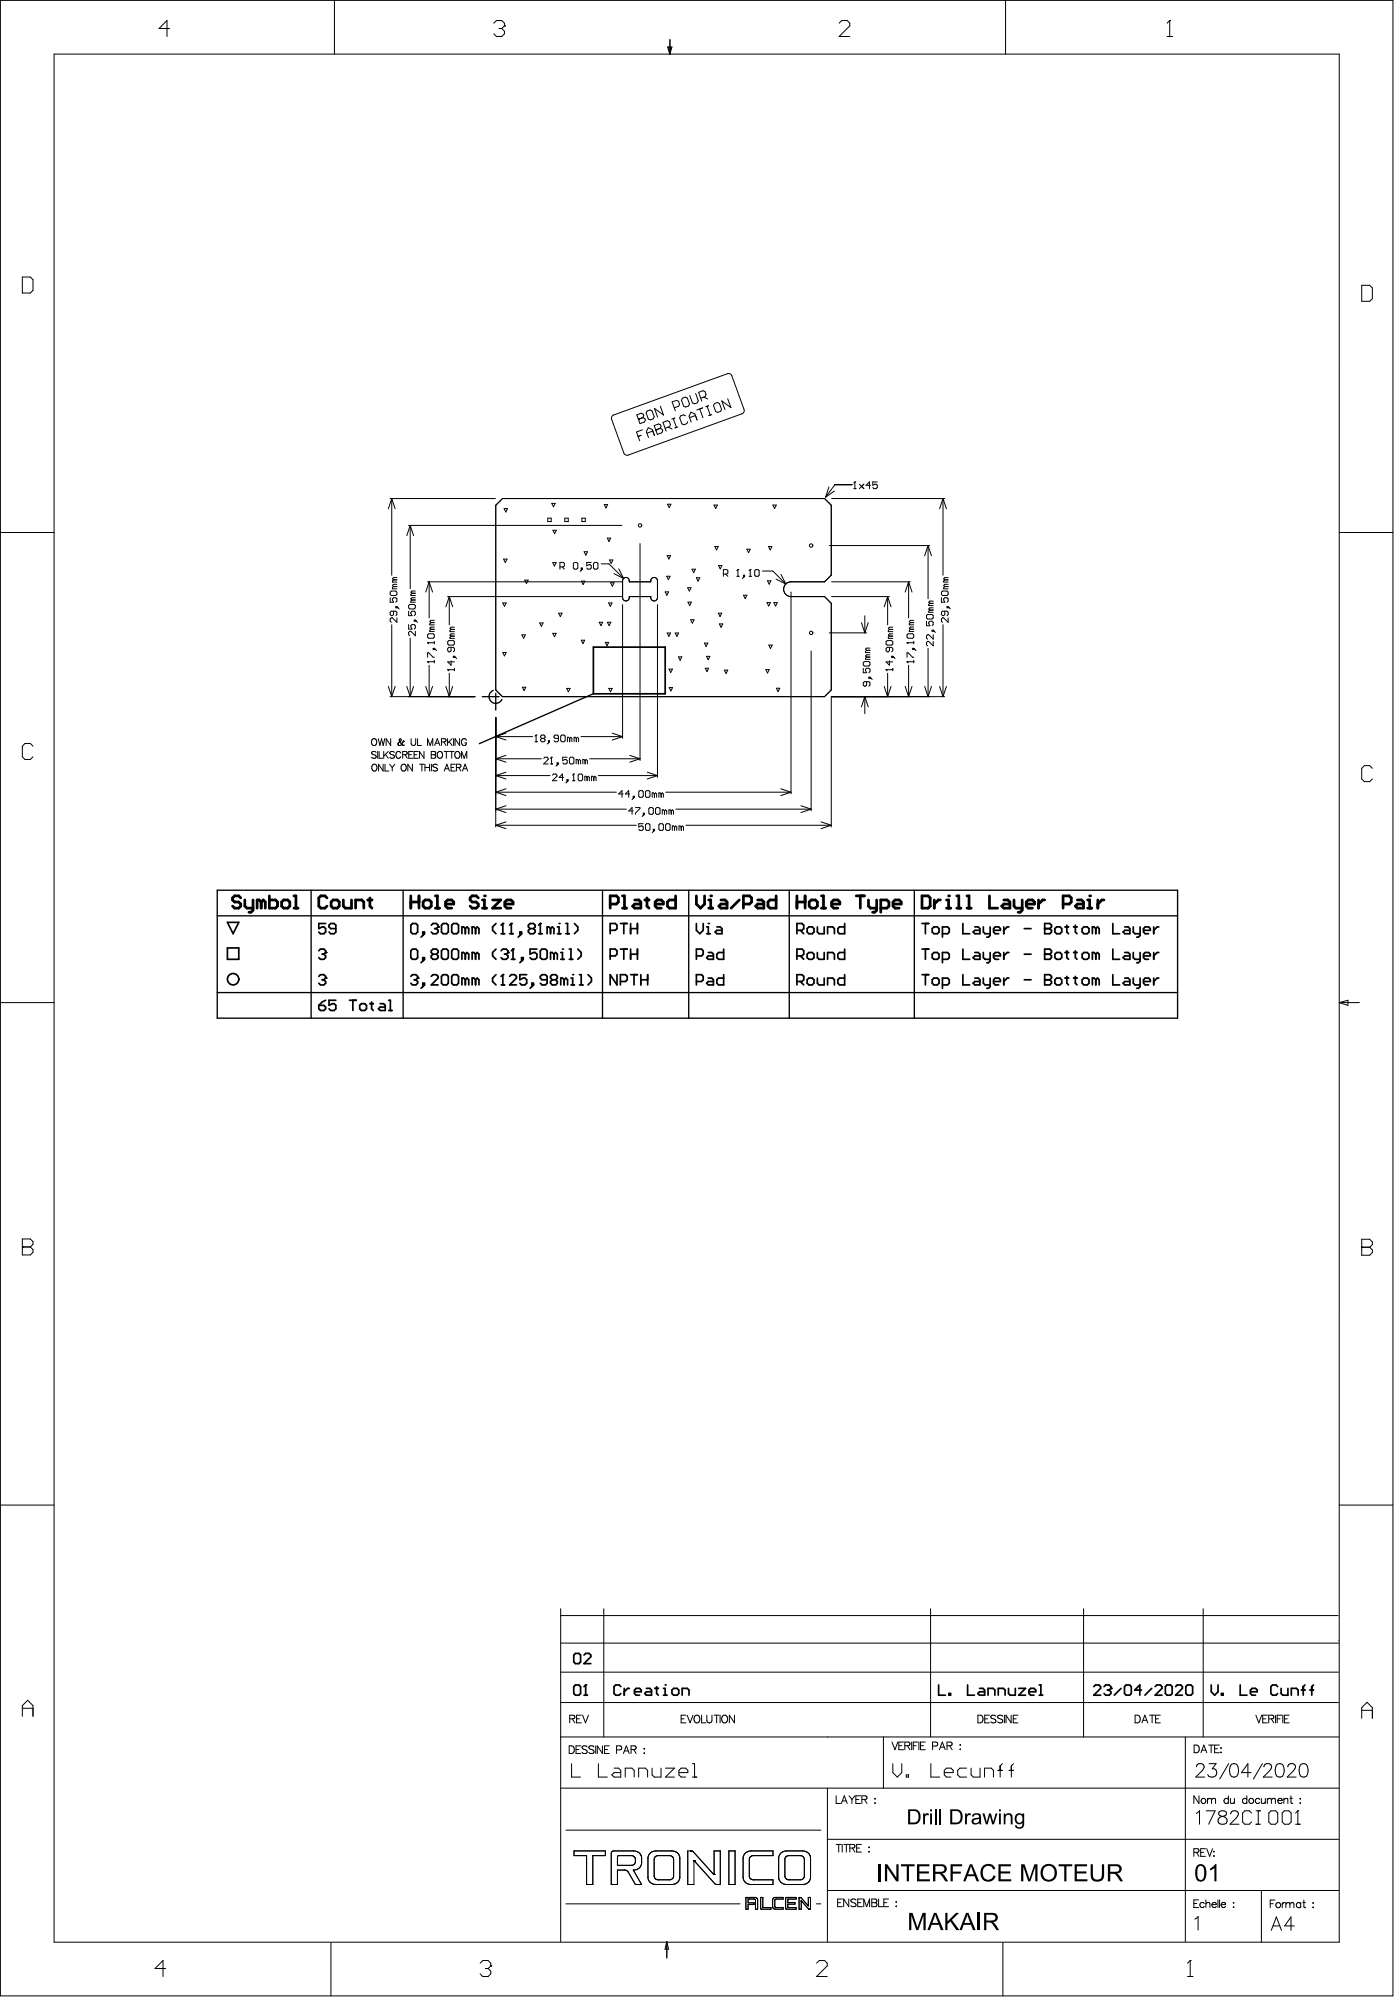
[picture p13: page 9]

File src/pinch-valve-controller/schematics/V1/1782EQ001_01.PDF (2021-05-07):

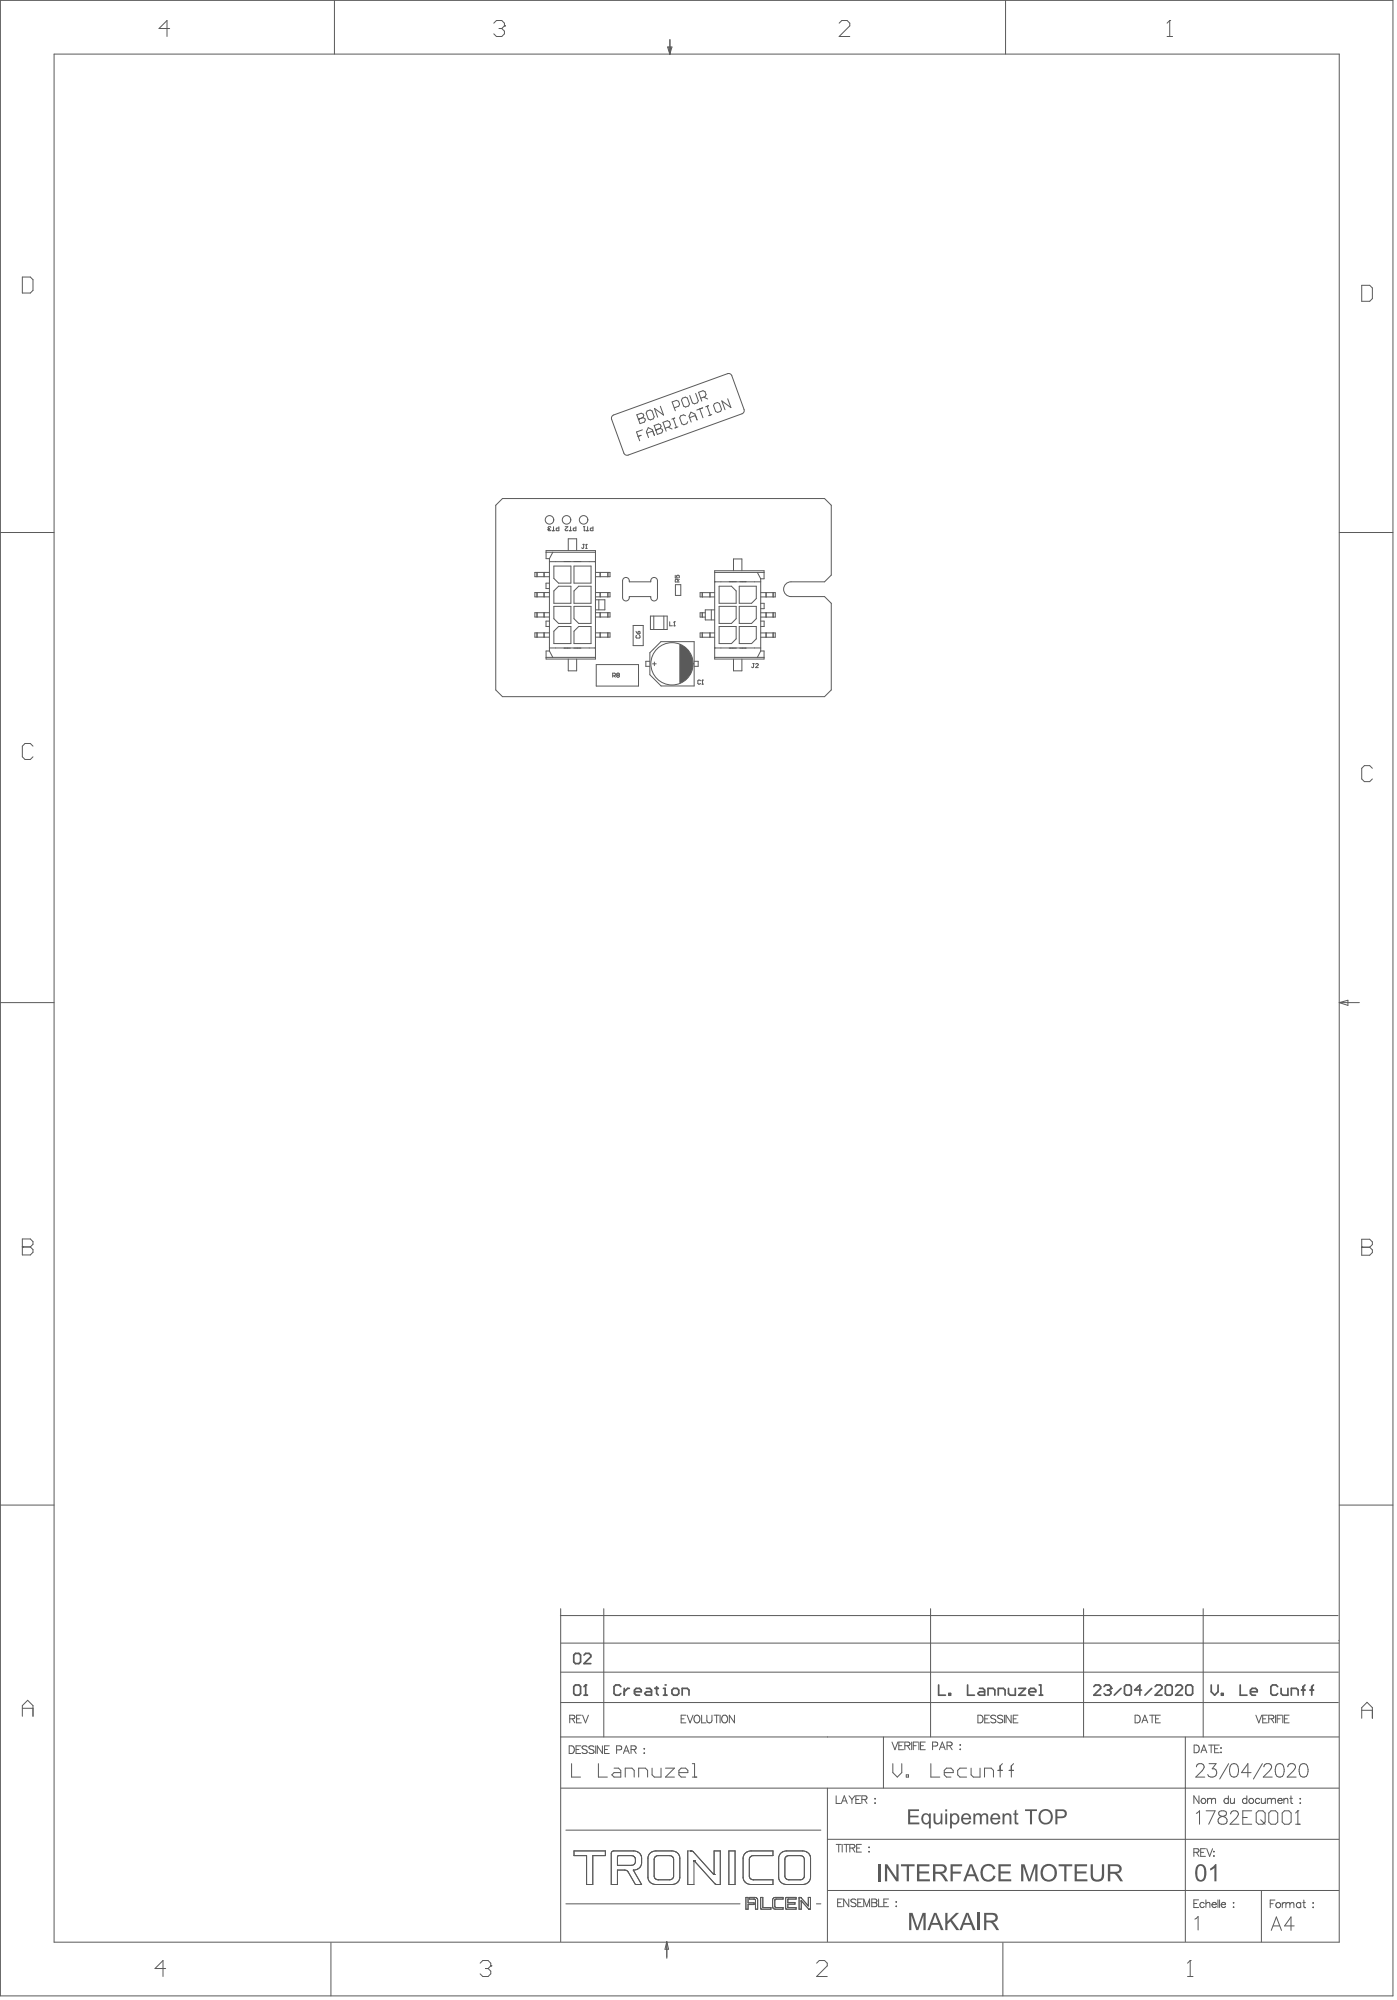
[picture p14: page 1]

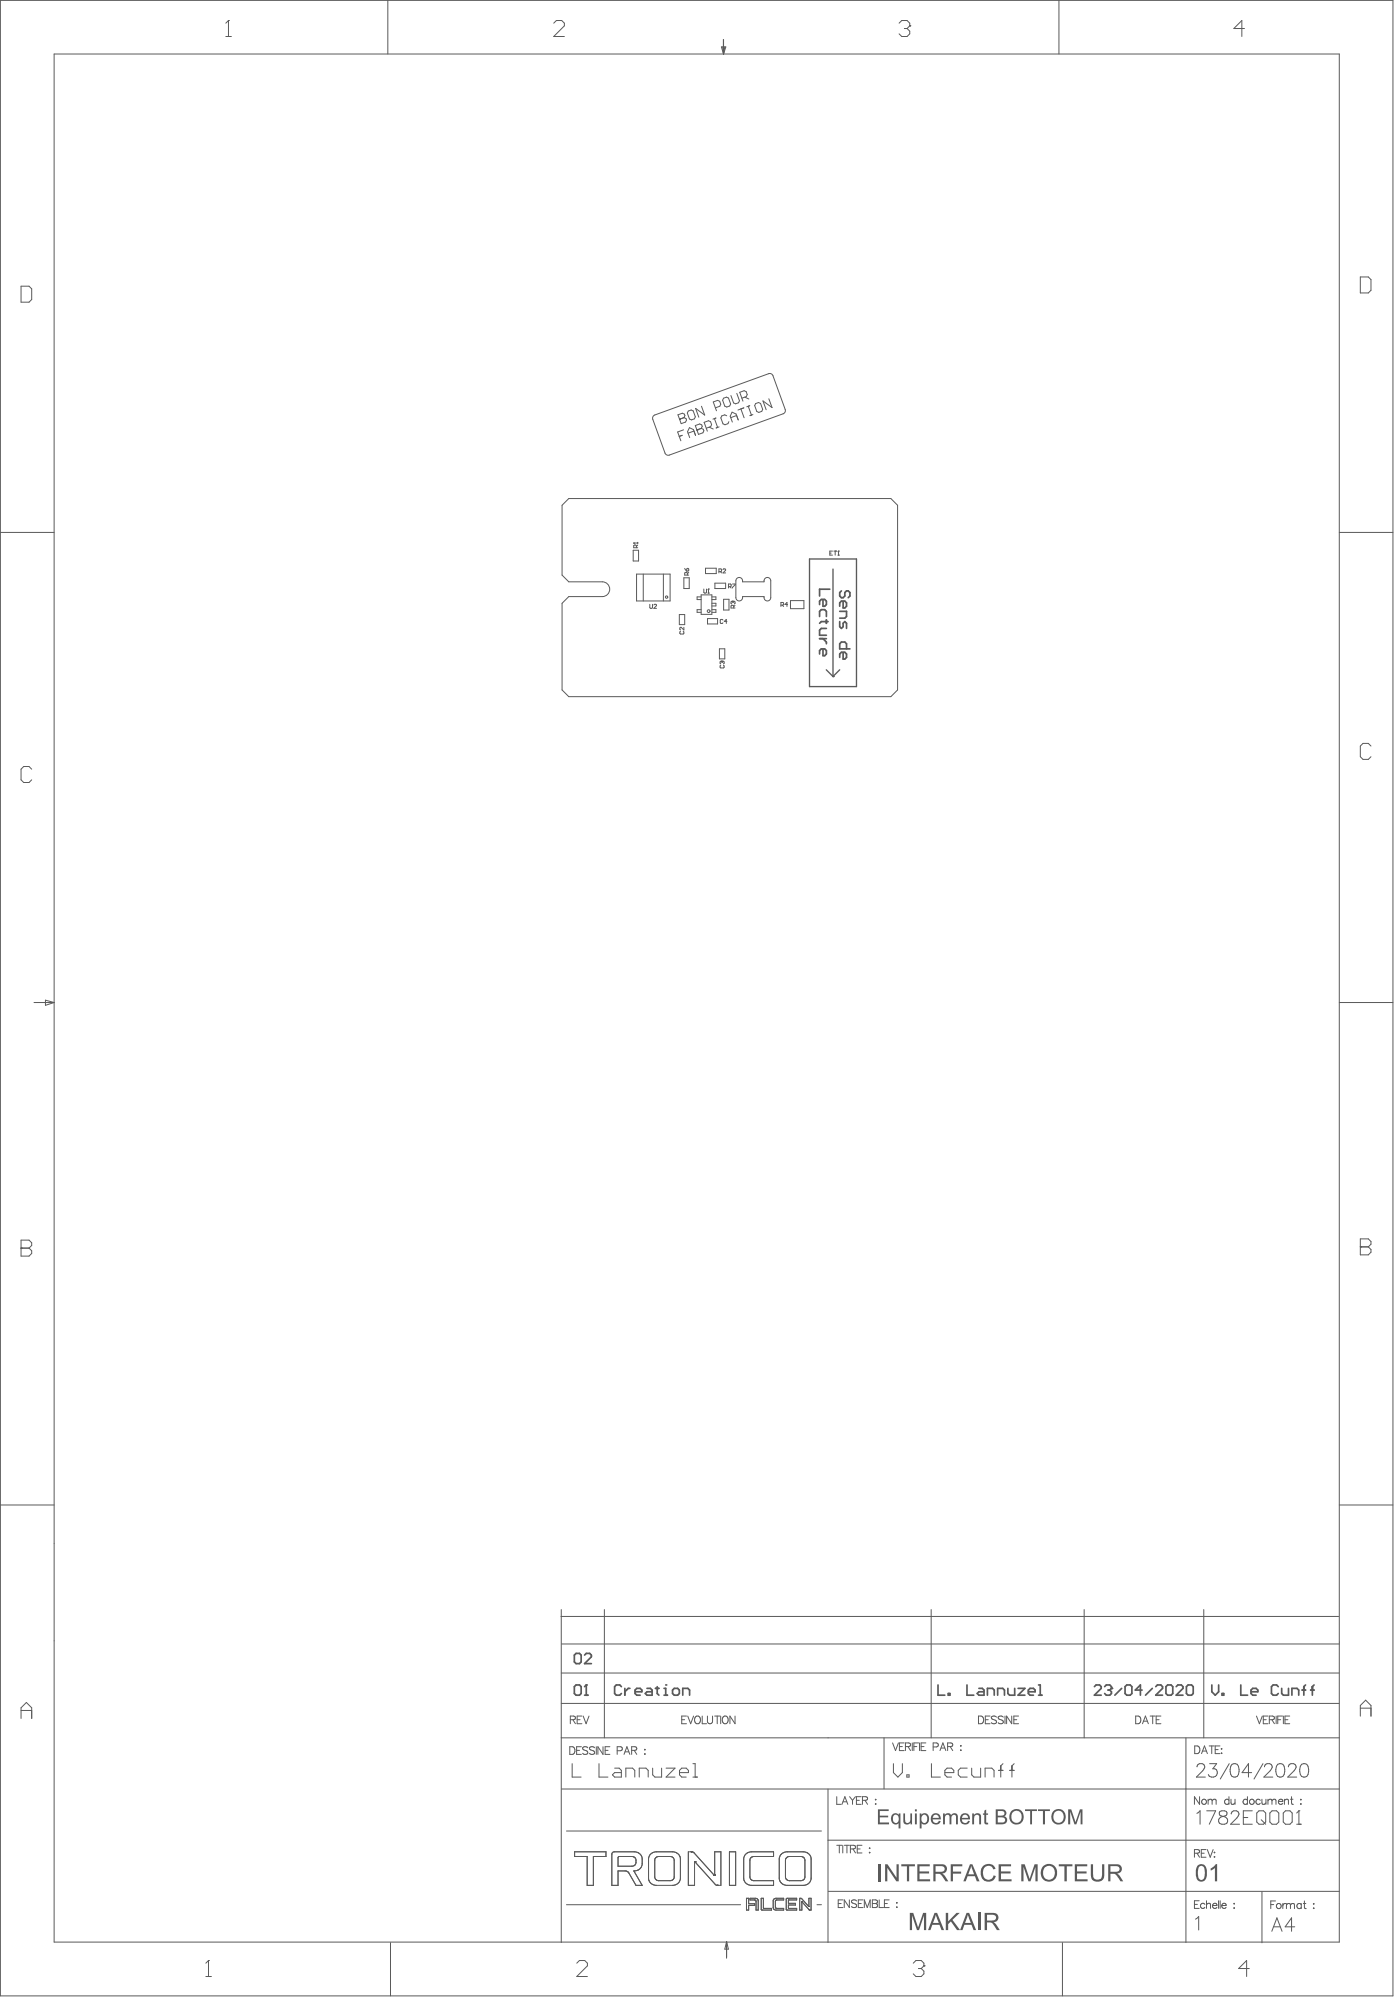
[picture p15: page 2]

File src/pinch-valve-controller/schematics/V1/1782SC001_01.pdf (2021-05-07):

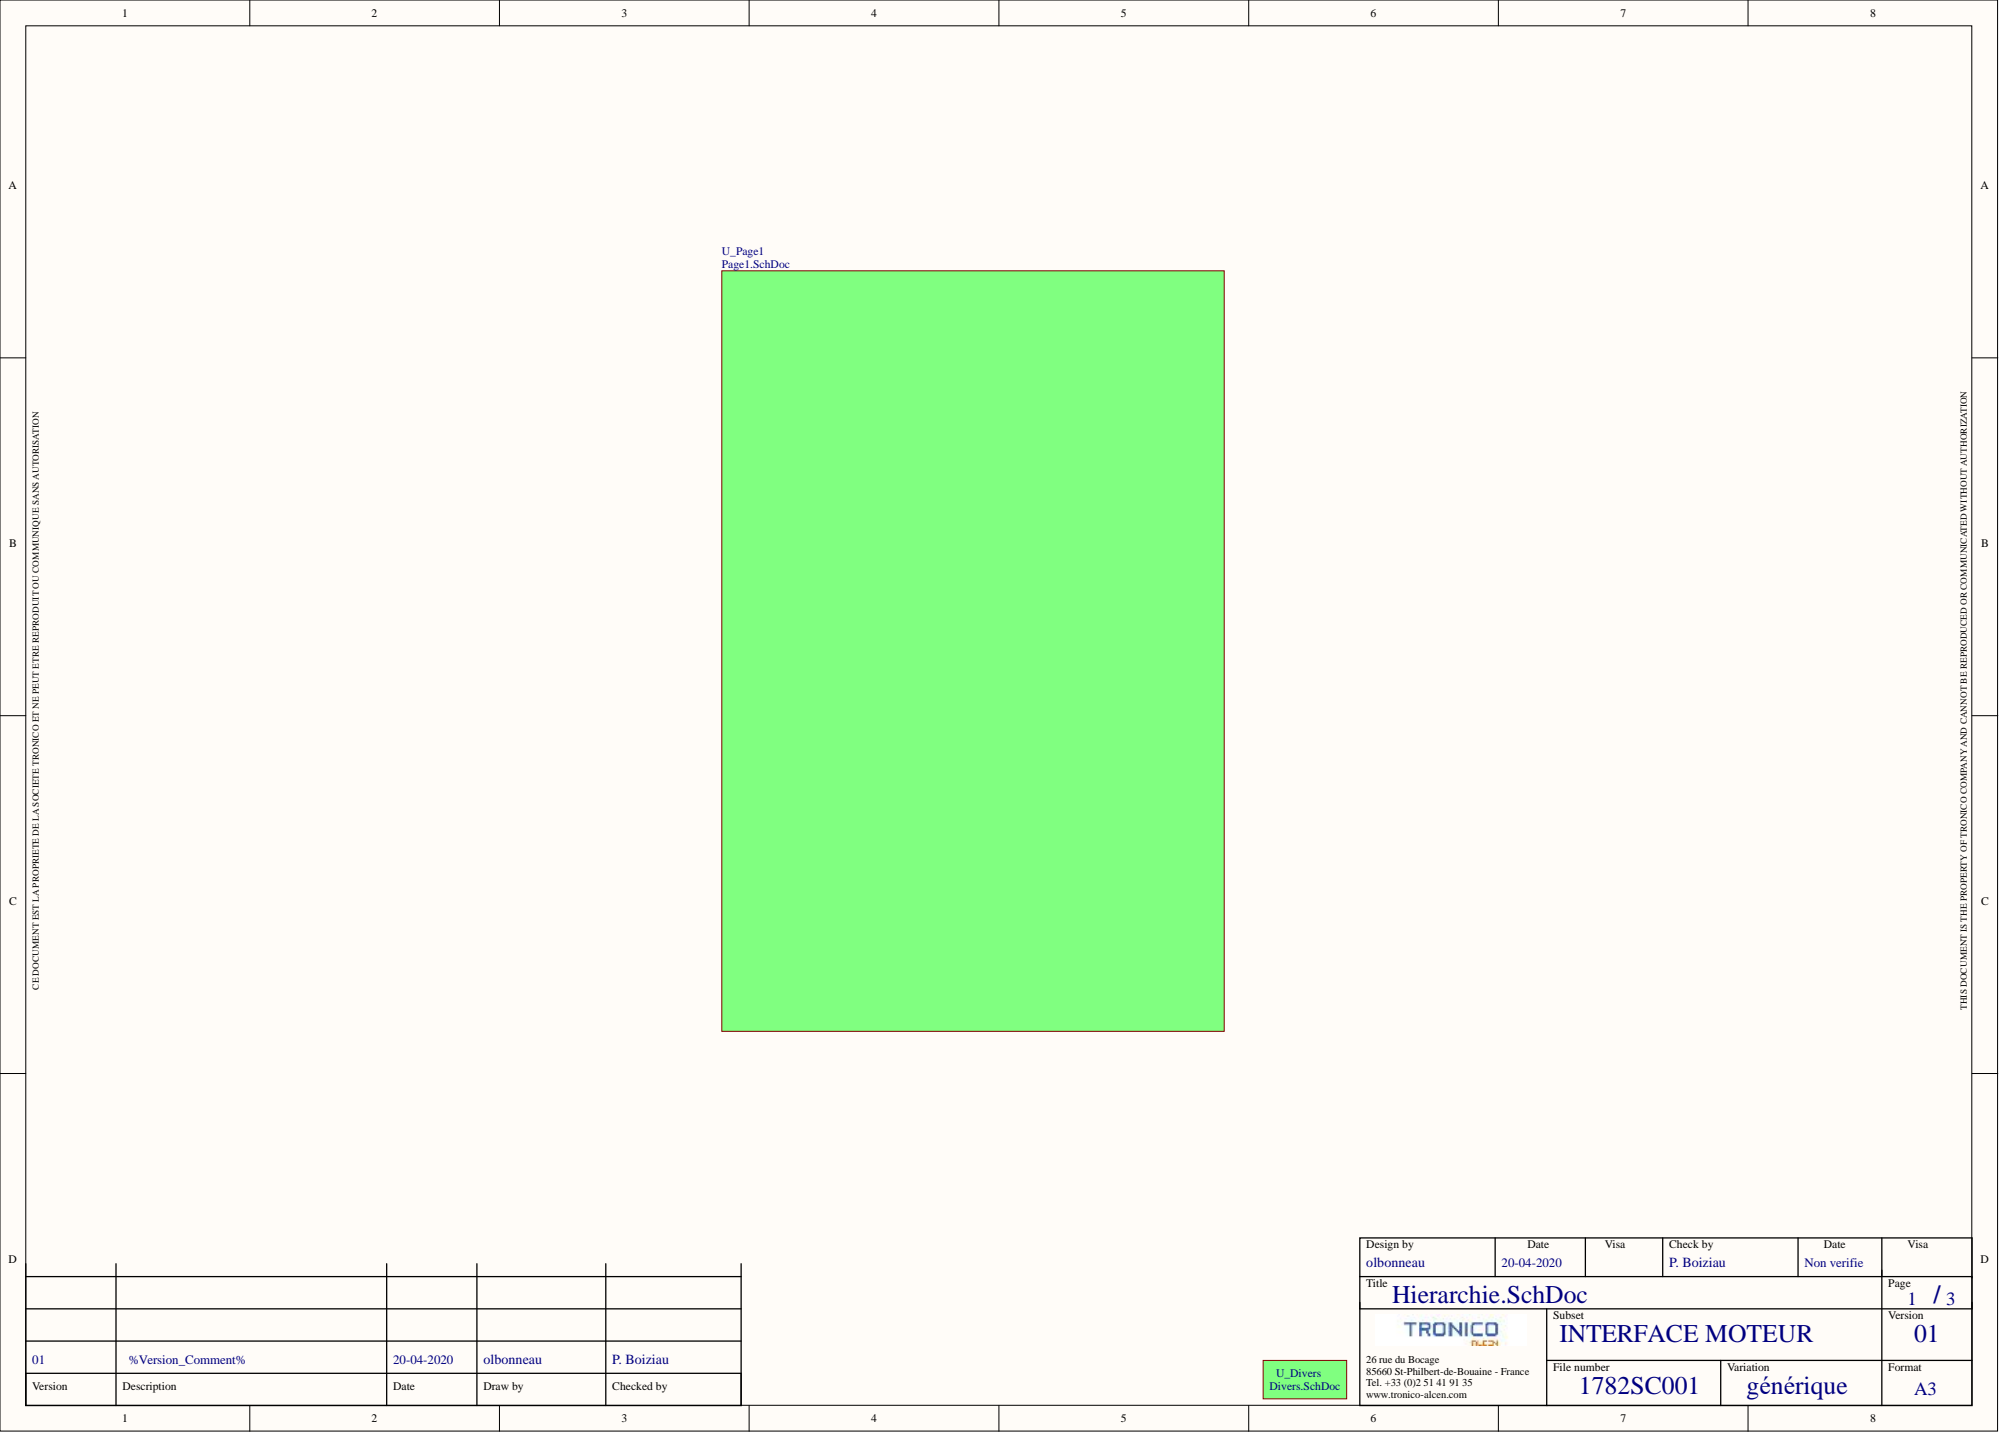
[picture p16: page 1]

THIS DOCUMENT IS THE PROPERTY OF TRONICO COMPANY AND CANNOT BE REPRODUCED OR COMMUNICATED WITHOUT AUTHORIZATION

CE DOCUMENT EST LA PROPRIETE DE LA SOCIETE TRONICO ET NE PEUT ETRE REPRODUIT OU COMMUNIQUE SANS AUTORISATION

Design by olbonneau | Date 20-04-2020 | Visa | Check by P. Boiziau | Date Non verifie | Visa

Title Hierarchie.SchDoc | | | | | Page 1 / 3

26 rue du Bocage 85660 St-Philbert-de-Bouaine - France Tel. +33 (0)2 51 41 91 35 www.tronico-alcen.com | Subset INTERFACE MOTEUR | Version 01

01 | %Version_Comment% | 20-04-2020 | olbonneau | P. Boiziau

Version | Description | Date | Draw by | Checked by


THIS DOCUMENT IS THE PROPERTY OF TRONICO COMPANY AND CANNOT BE REPRODUCED OR COMMUNICATED WITHOUT AUTHORIZATION

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


THIS DOCUMENT IS THE PROPERTY OF TRONICO COMPANY AND CANNOT BE REPRODUCED OR COMMUNICATED WITHOUT AUTHORIZATION

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

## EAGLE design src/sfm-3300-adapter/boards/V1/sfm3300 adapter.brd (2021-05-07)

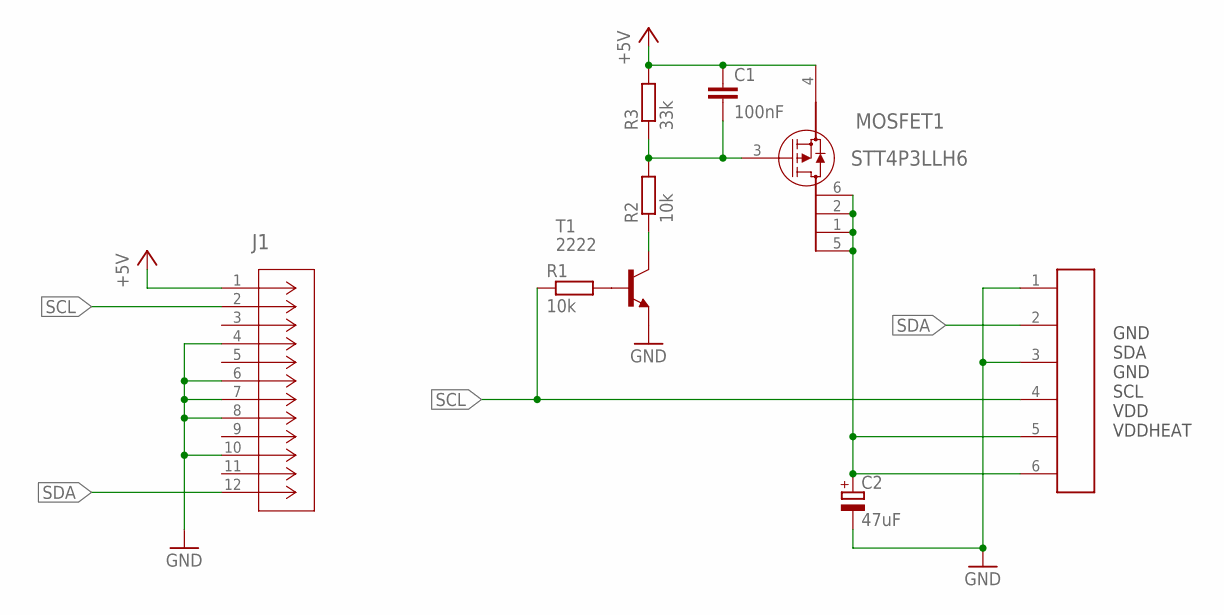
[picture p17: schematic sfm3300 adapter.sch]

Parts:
C1: 100nF; C0603
C2: 47uF; SMC_A
J1: 1-188275-2; CONN_1-188275-2_TYC
MOSFET1: STT4P3LLH6; SOT23-6L_STM
R1, R2: 10k; R0603
R3: 33k; R0603
T1: 2222; SOT23-BEC
U$1: SPRING6; SPRING-6

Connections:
+5V: C1.1, J1.1, MOSFET1.4, R3.2
GND: C2.-, J1.4, J1.6, J1.7, J1.8, J1.10, T1.E, U$1.1, U$1.3
unnamed: R1.2, T1.B
unnamed: C1.2, MOSFET1.3, R2.2, R3.1
unnamed: R2.1, T1.C
unnamed: C2.+, MOSFET1.1, MOSFET1.2, MOSFET1.5, MOSFET1.6, U$1.5, U$1.6
SCL: J1.2, R1.1, U$1.4
SDA: J1.12, U$1.2

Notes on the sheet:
GND SDA GND SCL VDD VDDHEAT

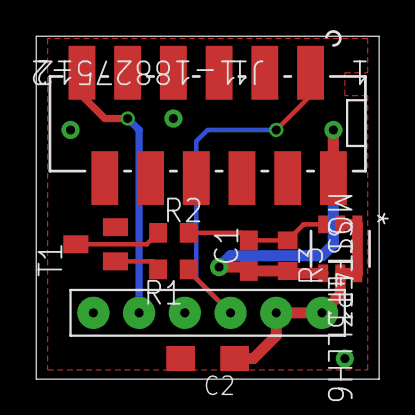
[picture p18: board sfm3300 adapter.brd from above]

Board: 2 copper layers, 19.1 x 19.0 mm, 9 parts (0 on the bottom side), 8 nets.

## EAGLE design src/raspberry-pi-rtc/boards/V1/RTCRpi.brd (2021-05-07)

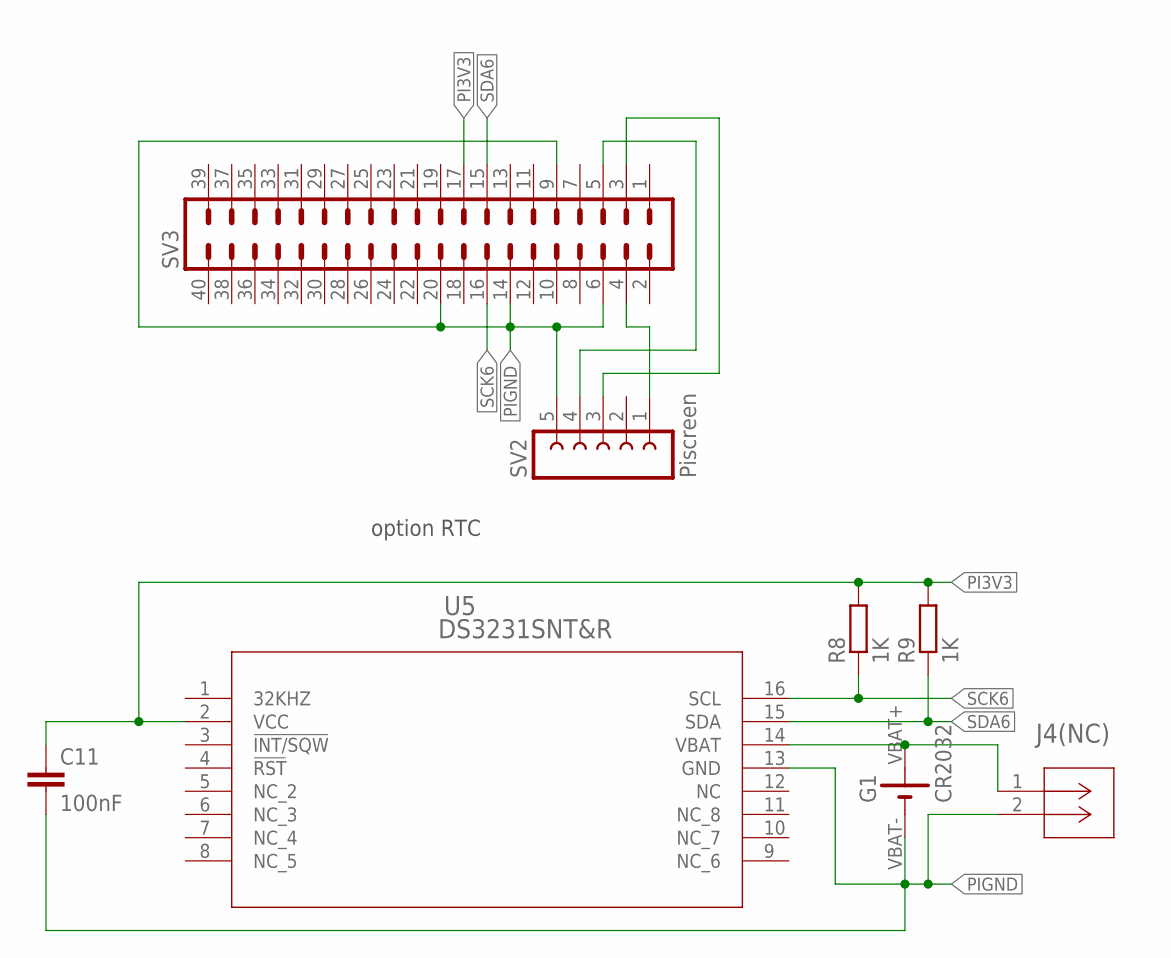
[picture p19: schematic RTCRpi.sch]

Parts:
C11: 100nF; C0603K
G1: CR2032
J4(NC): B2B-XH-A(LF)(SN); CONN_B2B-XH-A(LF)(SN)_JST
R8, R9: 1K; R0805
SV2: Piscreen; FE05-1
SV3: MA20-2
U5: DS3231SNT&R; 21-0042B_16_MXM

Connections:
unnamed: SV2.1, SV3.4
unnamed: SV2.4, SV3.5
unnamed: SV2.3, SV3.3
PI3V3: C11.1, R8.2, R9.2, SV3.17, U5.2 (VCC)
PIGND: C11.2, G1.VBAT- (-), J4(NC).2, SV2.5, SV3.6, SV3.9, SV3.14, SV3.20, U5.13 (GND)
SCK6: R8.1, SV3.16, U5.16 (SCL)
SDA6: R9.1, SV3.15, U5.15 (SDA)
VBAT+: G1.VBAT+ (+), J4(NC).1, U5.14 (VBAT)

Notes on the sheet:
option RTC

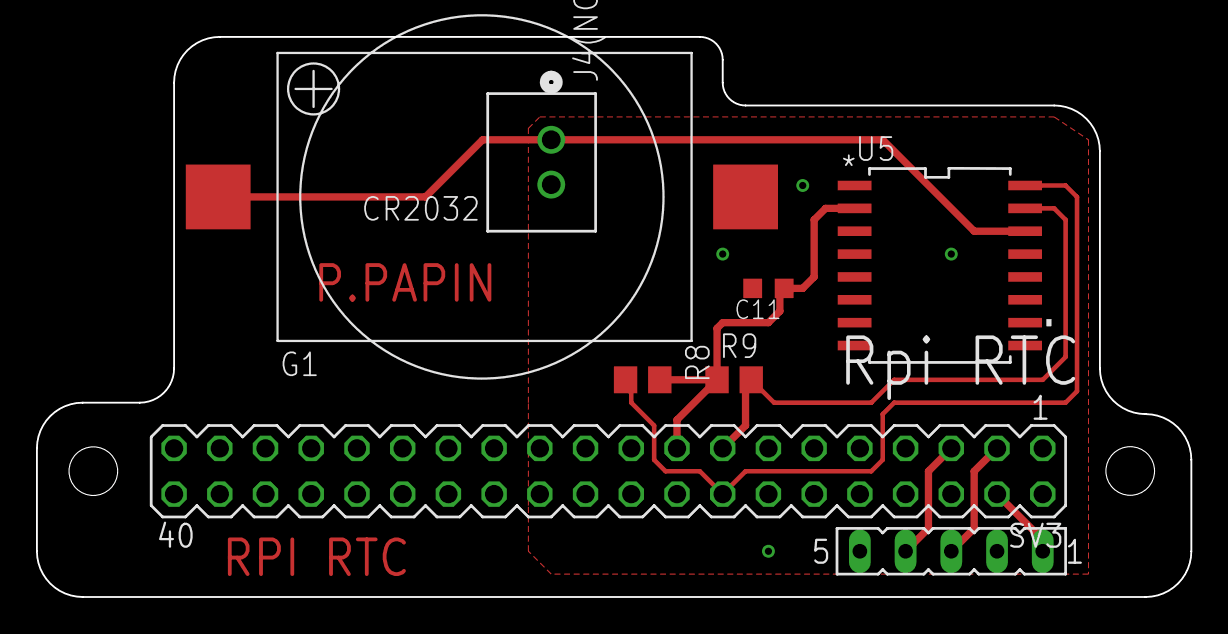
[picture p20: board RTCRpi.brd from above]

Board: 2 copper layers, 64.1 x 31.1 mm, 8 parts (0 on the bottom side), 8 nets.

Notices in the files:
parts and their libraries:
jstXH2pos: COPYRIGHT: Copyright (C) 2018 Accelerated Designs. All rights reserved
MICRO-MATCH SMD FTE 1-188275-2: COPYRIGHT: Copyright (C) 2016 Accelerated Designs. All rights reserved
